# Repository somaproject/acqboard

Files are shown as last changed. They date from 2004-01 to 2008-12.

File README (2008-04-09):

pcb/
    All Protel-related files for schematic capture and board design

docs/
    Documentation, including Adobe Illustrator design documents,
    graphs from final filter responses, and comments on design decisions
docs/filters
    Filter design and analysis and simulation code

vhdl/
    main system vhdl

sim/
    code to simulate the vhdl, and for spice sims
    .do files
    simulated parts (acqboard, etc)
    analysis of the output

tgt/ 
    Final aggregate project, compiled outputs, filters, bitstreams, etc. 

tests/ 
   code to test various parts of the system in the real world -- i.e. hardware tests, etc. 

tests/vhdl : 
   bits of vhdl for testing
tests/analysis : 
   code to analyzie the resulting output
tests/results :
   result data, result figures, result commentary
tests/acqboardcmd:
   program for interfacing with protoboard acqboard domain sockets
tests/benchmarks:
   The actual benchmarks; this is the code that generates and saves the results of a series of runs in HDF5 format. These files are saved to results, and analysized with analysis

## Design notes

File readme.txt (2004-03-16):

To do:

Change ADC buffer amps + filter stage into RRIO op-amps
Figure out some solution to the voltage problem. 

Simulations of butterworth input amps

So, there's this problem in that the system, as designed, uses non-RRIO adc buffer op-amps (the AD8021). This sucks, a lot. 

Because if we want to level-shift our input +-2.5 to 0-5V unipolar, we need a RRIO buffer. Plus, there are (IMHO) issues with the adc reliably sampling stuff that gets too close to its rails. 

So, ideally, the ADC could sample 0-4.096 V, and the inputs could be limited to +-2.048 V. Which is great, just switch in a new voltage regulator. We'll still
have to design-in a new buffer amp, but whatever, it may not really need to be RRIO if it can go to within 1V of the rails. 

But how do we find a 1.024V  voltage reference fto bias the buffer OAs?. Accuracy (as in initial, and TCO) isn't that big of a deal because it will
all be taken care of digitally. But the Ibias Is pretty high, and i'm not sure how it varies with amplitude, etc. 

Now, to pick a new Op-Amp:

part	price/160  Ibias (nA)	Vnoise	Voffset	SFDR	notes
AD8027		   4000/6000	
AD8510		   0.075				input v from -2 to +2.5
AD8671		   40		3	75		VOUT too low
AD820							Crappy THD+N
AD8651							VOUT too low
AD8627						-90 

Ha ha, we can just use the AD8027 :) We just need to buffer the voltage-divided reference through an OA. Although, ass, it's performance is mediocre in the THD+N measurement. 

However, the AD8519 supposedly has THD+N in unity gain of 120 dB, although there aren't really graphs. But it will most certainly work as an ADC driver, assuming that the voltage inputs aren't an issue. 

Now, for some math: 
our voltage reference is accurate to 0.1%, and drifts at 25 ppm/C
Resistors for dividing: 0.1%, drift 25 ppm/c

After contacting people, it looks like I may just be SOL wrt getting tempco-matched resistors.  But I can find 25ppm/C ones. 

Now, let's assume values of 10k each, and let's assume that TCo is positive. Now, the tempcos are potentially going to co-vary, because they are in close physical proximity. But ignore that -- let's assume R2 stays constant, and R1 varies at 25 ppm/C, for maximum difference. That works out to Vout = Vin(1+Tco)/(2+Tco), or (for 25 ppm/c) roughly 6 ppm/C. This puts a lot of the responsibility for stability on the voltage reference. We can use a OPA227 to buffer the output. 

--------------------------------------------------------------------------
Soma Command configuration
--------------------------------------------------------------------------
The soma command interface over fiber is spartan at best. 

Each transmit packet has a CMDST byte, a CMDID byte, and a CHKSUM byte.

The acqboard can be in one of three modes:
    Mode 0: normal mode, acquiring and filtering data. 
    Mode 1: offset disable -- dc offset compensation is disabled
    Mode 2: disables the input and disables offsets. Just outputs programmed sample buffer. 

Each of these modes has a "loading" bit.

Note that there is this "problem" with there only being one acqboard interface but two DSPs. this means channel modification commands have to be very careful!!!

--------------------------------------------------------------------------
So, general system properties, etc: 

AD8221 has amazing stuff... the new data sheet is an inspiration to all of humanity!

--------------------------------------------------------------------------
AA Filter component value selection:
--------------------------------------------------------------------------

For the LTC1653-3, the equation is:
R = 10k * (256kHz)/Fc; 

from the dsp folder:

The first filter has a -3 db at 10056.32 Hz
The second filter has a -3 db at 29829.14 Hz
The combined (both) filter has a -3 db at 9605.82 Hz
The combined (both) filter has a -96 db at 129371.07 Hz

We assume that their Fc == -3 dB point, thus 
The LTC1563-3 Resistors are 255k , part 9C08052A2553FKHFT from digikey

---------------------------------------------------------------------------
input stage
---------------------------------------------------------------------------
499 0hm .5% \0805 resistors, RR12P499DCT-ND from digikey

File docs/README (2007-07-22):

    * Overview

    *CHAPTER 1 Problem formulation (Design goals and overview)
          o What our real goal is
          o The importance of
                + Linearity
                + Linear Phase
                + Low-noise
                + High common-mode rejection
                + potential DC accuracy?
                + Bandwidth?
                + Resolution
          o Size?
          o Programmable Gain
          o Cost?
          o Number of channels
      
          o Electrical Isolation -- the challenges of mixed-signal design

    * CHAPTER 2 signal chain design -- all design data 
      -- these are all the design specs; there is no empirical data here at all
      * schematic of signal channel 
      * input: In-Amp -- component and performance
      * Amplification : PGA, filter
         * gain settings / voltage ranges
      * Continuous channels: 
      * A->D:
         * Hardware Filter design:
	   o We desire 16-bit resolution with an input bandwidth of 10 kHz. 
	   o to achieve this, we oversample, downsample, and filter
	
         * digital filtering 
	   * digital filtering simulation
	   * fixed-point math 

    * CHAPTER 3 Measured performance:
      1. CMRR  
      2. Noise
      3. THD+N 
      4. linearity 
      5. Rat Data

    * CHAPTER 4 Board operation and fiber IO 
          o four modes
            1. describe modes
          o output interface
          o input interface and bus protocol
          o actual commands
	  o front and back interfaces? 
    * CHAPTER 5 digital hardware implementation -- A tour of the FPGA
          o FPGA selection
          o Digital offsets
          o fixed-point math
          o Commands
          o Optical Interface
          o Modes
          o EEPROM functionality

    * CHAPTER 6 Circuit Design Commentary, hardware
 	* Schematics, what they mean? Component identification?
 	* PCB Layout 
 	  * composit diagram -- tour, showing modules, layers
   	  * ref appendex in the back 
        * BOM
        * Component identification
	* enclosure
  	
    * Additional Results
          o [additional simulation notes]
          o Tests on:
                + Analog performance, using Chris's hardware (?)
                + Single-channel
                + multi channel
                + Real Rat

Albert suggests appendix

    * THD+N measurement mechanism
    * Oversampling, downsampling, etc. 
    * Filter design code, analysis
    * 

Points we'll want to be sure to discuss someplace: 
Component identification process
Parameters measured
VHDL organization
unit tests
Raw mode
offset calibration

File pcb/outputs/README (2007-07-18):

the files are

acqboard.GTO : top silkscreen
acqboard.GTS : top soldermask
acqboard.GTL : top solder layer
acqboard.GP1 : internal plane 1
acqboard.GP2 : internal plane 2
acqboard.GBL : bottom solder layer
acqboard.GBS : bottom soldermaskk
acqboard.GBO : bottom silkscreen
acqboard.TXT : drill file

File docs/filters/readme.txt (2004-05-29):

-- files in this directory
analogfilters.m : calculations and graphs of the analog filters on the board,
		 and combines them with an in-memory variable called "h", 
		 that is, the impulse response of the FIR decimating filter. 

fxquant.m : _so_ not my code. code to quantize the coefficients in an intelligent way. 
	  
vect_to_block_22 : takes a vector of type double normalized to between -1 and 1, quantizes the values to acceptable 22-bit twos-complement fixed point values, and then writes out those values in hex optimized for copying into blockselect+ ram. 

------------------------------------------------------------------------------
Signal processing related to the Soma acquisition board. 

First, we need a digital low-pass decimating filter which will (for data sampled at 256kHz) pass t400o 10 kHz with as little ripple as possible, and stop at 16 kHz down by ~85 dB. Why 85 db? The analog filters have already attenuated atthat point, and monotonically attenuate after that.  

Oh, and max it can only be 120 taps long. 

h_01.mat : good example of filter.
h_02.mat is another good example. The problem is that we still aren't getting the response we want, but this'll be good enough. 

for our analog filters, they are approximated by:

[bf2, af2] = besself(2, 38000);
[bf1, af1] = besself(4, 15250);

such that :

The first filter has a -3 db at 10056.32 Hz
The second filter has a -3 db at 29829.14 Hz
The combined (both) filter has a -3 db at 9605.82 Hz
The combined (both) filter has a -96 db at 129371.07 Hz

Using the equations fomr SLOA049A for a second-order bessel with:
order 2
FSF=1.2736
Q=.5773

we know R2=R1, thus the big variables are R2, R3, C1, and C2. 
Fc=1/(FSF*2*pi*Q*(R3*C1+R2*C1+R3*C1)); 
C2=(Q*(R3*C1+R2*C1+R3*C1))^2/(R2*R3*C1)
so (per the app note)

R2=1.870 k = R9 = R8
R3=1.870 k = R10
C1=1300 pF = C42
C2=3900 pf = C44

-----------------------------------------------------------------------------
more DSP
-----------------------------------------------------------------------------

note that the output ft following decimation is

Y_d(e^{j\omega}) = \frac{1}{M}\sum_{i=0}^{M-1}X(e^{j(\frac{\omega}{M}-\frac{2*pi*i}{M})})

I.e. added, replicated copies. Thus, we created the function downspectra, which adds the spectra of a filter h[n] downsampled by N, scaled by the appropriate amount, and returns the result, from 0 to pi. 

As we can see from the output of downspectra.m, the aliased images suck a lot more than we had originally anticipated, because there are 7 of them adding up. Thus, it's not enough to make sure our signal outside of the bandwidth of interest is down by 96 db, but rather need an ADDITIONAL 15 dB down!

But, we only care about the region in DC-10 kHz, correct? So... 

First, we created some code to let us look at downsampled filters.

Then, we realized that we could:
B = remez(119, [0 10/128  22/128 1], [1 1 0 0 ], [0.5  1000]);
I.e. create a filter with a not-as-tight passband. this results in us getting part of a high-frequency image in our output, but "who cares", as we're only interested in the band between 0-10 khz. This will mean, however, that all DSP boards will need to have an O(10) tap filter to further filter. Oh well. 

Part of me still wishes there were a better way. I'm just not seeing it though. But, happily, we now have correct output plots of the signal versus alias/noise for the total system. 

The better way was to allow filters of length 144. 

If we allow filters of this length, then we can alias-away the problems.

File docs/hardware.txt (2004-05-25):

To do:

Change ADC buffer amps + filter stage into RRIO op-amps
Figure out some solution to the voltage problem. 

Simulations of butterworth input amps

So, there's this problem in that the system, as designed, uses non-RRIO adc buffer op-amps (the AD8021). This sucks, a lot. 

Because if we want to level-shift our input +-2.5 to 0-5V unipolar, we need a RRIO buffer. Plus, there are (IMHO) issues with the adc reliably sampling stuff that gets too close to its rails. 

So, ideally, the ADC could sample 0-4.096 V, and the inputs could be limited to +-2.048 V. Which is great, just switch in a new voltage regulator. We'll still
have to design-in a new buffer amp, but whatever, it may not really need to be RRIO if it can go to within 1V of the rails. 

But how do we find a 1.024V  voltage reference fto bias the buffer OAs?. Accuracy (as in initial, and TCO) isn't that big of a deal because it will
all be taken care of digitally. But the Ibias Is pretty high, and i'm not sure how it varies with amplitude, etc. 

Now, to pick a new Op-Amp:

part	price/160  Ibias (nA)	Vnoise	Voffset	SFDR	notes
AD8027		   4000/6000	
AD8510		   0.075				input v from -2 to +2.5
AD8671		   40		3	75		VOUT too low
AD820							Crappy THD+N
AD8651							VOUT too low
AD8627						-90 

Ha ha, we can just use the AD8027 :) We just need to buffer the voltage-divided reference through an OA. Although, ass, it's performance is mediocre in the THD+N measurement. 

However, the AD8519 supposedly has THD+N in unity gain of 120 dB, although there aren't really graphs. But it will most certainly work as an ADC driver, assuming that the voltage inputs aren't an issue. 

Now, for some math: 
our voltage reference is accurate to 0.1%, and drifts at 25 ppm/C
Resistors for dividing: 0.1%, drift 25 ppm/c

After contacting people, it looks like I may just be SOL wrt getting tempco-matched resistors.  But I can find 25ppm/C ones. 

Now, let's assume values of 10k each, and let's assume that TCo is positive. Now, the tempcos are potentially going to co-vary, because they are in close physical proximity. But ignore that -- let's assume R2 stays constant, and R1 varies at 25 ppm/C, for maximum difference. That works out to Vout = Vin(1+Tco)/(2+Tco), or (for 25 ppm/c) roughly 6 ppm/C. This puts a lot of the responsibility for stability on the voltage reference. We can use a OPA227 to buffer the output. 

--------------------------------------------------------------------------
Soma Command configuration
--------------------------------------------------------------------------
The soma command interface over fiber is spartan at best. 

Each transmit packet has a CMDST byte, a CMDID byte, and a CHKSUM byte.

The acqboard can be in one of three modes:
    Mode 0: normal mode, acquiring and filtering data. 
    Mode 1: offset disable -- dc offset compensation is disabled
    Mode 2: disables the input and disables offsets. Just outputs programmed sample buffer. 

Each of these modes has a "loading" bit.

Note that there is this "problem" with there only being one acqboard interface but two DSPs. this means channel modification commands have to be very careful!!!

--------------------------------------------------------------------------
So, general system properties, etc: 

AD8221 has amazing stuff... the new data sheet is an inspiration to all of humanity!

--------------------------------------------------------------------------
AA Filter component value selection:
--------------------------------------------------------------------------

For the LTC1653-3, the equation is:
R = 10k * (256kHz)/Fc; 

from the dsp folder:

The first filter has a -3 db at 10056.32 Hz
The second filter has a -3 db at 29829.14 Hz
The combined (both) filter has a -3 db at 9605.82 Hz
The combined (both) filter has a -96 db at 129371.07 Hz

We assume that their Fc == -3 dB point, thus 
The LTC1563-3 Resistors are 255k , part 9C08052A2553FKHFT from digikey

---------------------------------------------------------------------------
input stage
---------------------------------------------------------------------------
499 0hm .5% \0805 resistors, RR12P499DCT-ND from digikey

----------------------------------------------------------------------------
High pass Filter
----------------------------------------------------------------------------
Goals:
We use the OPA227UA in-amp as a 2-pole HPF

Rational for design: Assume that there's a 5 V difference between the output node and the input pin of the opamp. That means that there's a 5V drop across Ron+R1. But, then, the voltage across Ron varies as Ron/(Ron+R1). I.e. if R5 = 5k, ad max Ron = 50 ohms, then Ron will see 1/100th the voltage difference, and (as far as I can tell from the 

We end up with a first-order HPF with a pole at 1/RC. Assume Rs = 5k, and thus, we want HPF at:

50 Hz	 0.82 uF
200 Hz   0.22 uF
500 Hz = 0.12 uF

----------------------------------------------------------------------------
FPGA to S-3 in a day!
----------------------------------------------------------------------------
18 April 2004
So, today I'm going to explore the possibility of switching tothe 100-pin Spartan-3 -50 device. Why? 

1. A pack of 24 is only $18.00 each, and that price will come down
2. In 3 years, I'm sure they'll still be around, but cheaper. 
3. since I can get a large quantity now, availability isn't as much of a concern
4. They have dedicated 18x18 hardware multipliers, which should actually save me a lot of space. 
5. I'm wasting time worrying about this "does it fit" mentality -- I hope the mulipliers will save me enough space that the device will easily fit in this logic.  
6. They have a ton more ram (4x) which enables longer filters. This is a good thing because at the moment, I'm capped at a 120-tap filter. This sucks, because it will force me to use the approach for output frequency response I was considering earlier. 

basically, I don't just want stuff down by 96 dB at the 16 kHz edge, because 7 additional copies of the stopband are going to alias into my passband. But given length constraints on h[n], it was impossible to get a FIR filter with a stopband ~-110 dB down. The solution was to push the stopband start out to 19 khz, which would yes, allow for aliasing into the 10-16 kHz region of up to -20 dB. But we only cared about the 0-10kHz region.

Why this is a poor design decision: your output, by design, will have aliasing in the 10-16 kHz range, meaning that the output of the acqboard isn't "safe", i.e. it would need knowledgable post-processing to deal properly. 

Switching to a Spartan-3 lets me eliminate this by using a longer filter, giving me the 10-16 kHz response I need. 

7. It shouldn't take very long to make the switch; go modular design!

The multiplier in the current design (not including the accumulator) takes up 342 slices, i.e. 312 flip flops and 366 LUTs. That's 44% of the design!

There are three things we'll need to change:
1. RMAC hardware: 
    switch multiplier to use the 18x18 hardware mults
    change expected pipeline delay
    So, it looks as if, since XST is inferring things correctly, we don't need to actually explicitly declare them. This strongly suggests that our pipeline delays haven't changed either. 

2. Buffers.
   Each BlockSelect+ ram block has 4x the ram of one in a Spartan-IIE, but there are half as many. The net result is that we have double the ram we did before. We want to effectively double the amount of storage for each buffer, i.e. 256 16-bit words. This means each BlockSelect+ ram block can hold 4 buffers. We will need 3 of them to store all sample buffers. This will also necessitate widening the AIN, AOUT busses from 7 to 8 bits. 
  Added extra pipeline stage to meet timing requirements. 
3. Filter
   Simple to do with a single buffer. 
  Added extra pipeline stage to meet timing requiremetns. 

4. EEPROM interface
   Remapped some of the EEPROM so the loader can still sequentially load stuff. 
5. Control
   Had to be modified as a result of the new EEPROM addrs. Note now that we use DATA[7:0] 

Debug -- adding an extra mode. We're going to add a new "RAW" mode that will just take a single channel and output all of its 256 ksps.

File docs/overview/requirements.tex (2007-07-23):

\section{Requirements}
The Acquisition Board was designed with multiunit electrophysiology in
mind. Below is an explanation of the various design parameters as well
as the context within whcih they are evaluated.

\subsection{Differential Amplification}
All electrophysiological measurements are measurements of an electric
potential -- a voltage. This voltage must be measured between two
points, Va and Vref (the latter being a reference). Frequently
additional sources of voltage relative to ground are present on both
of these inputs, generated by uncontrolled environmental sources. This
\textit{common-mode voltage} is common to both inputs, and is ultimately
removed by the differential amplification.

In practice, manufacturing tolerances prevent complete removal of
common-mode voltage. The ability of a differential amplifier to remove
common-mode voltage is expressed as a ratio of...

\subsection{Input range, amplification, and resolution}

The potential voltages encountered in neural systems can
vary over orders of magnitude. Even when measuring the same
phenomina, differences in electrode configuration and reference
placement can result in a tenfold difference in required
amplification. Thus, electrophyisology amplifiers are equipped
with programmable gain amplifiers, allowing a selection of input
amplifications. 

The existing equipment in MWL allows for 12-bit sampling
of input voltages with full-scale 20 mV (gain = 1,000) to 500 uV
(gain = 40,000). This allows for LSB sizes between 4.8 mV and
122 nV, although system noise performance makes the latter
number unattainable.  

\subsection{Bandwidth}

Electrophysiological phenomina in the brain can be losely divided into
high-frequency, discrete events and low-frequency, continuous signals.
Neural action potentials ("spikes") comprise the first category, with
frequencies of interest between 1 kHz and 8 kHz. Electroencephalogram
and local field potentials are believed to be the aggregate
synchronous activity of large brain regions, and make up the bulk of
the latter group. These slower-wave signals extend from 200 Hz down to
near-DC levels.

Thus any electrophysiological system will need to be able to isolate
the higher-amplitude, low-frequency EEG from the low-amplitude,
high-frequency spikes, and do so using controlled filtering that
prevents saturation of analog-to-digital converter input. An aggregate
bandwidth of 10 kHz is thus necessary.

\subsection{Noise}
Even in the absence of any common or differential input, all
amplifiers still generate internal electrical noise, which is measured
relative to the input. This noise corrupts input signals and is
generally broadband, thwarting computaitonal attempts at removing it.
Input noise can directly contribute to cluster size for multiunit
recordings, making unit isolation more difficult.

Our current amplifiers have a manufacturer-measured RTI noise of 20 uV
peak-to-peak. This can have a substantial impact on recorded peak
amplitude of a common 200 uV spike. Ideally, Soma would cut this noise
amplitude down by a factor of 10.

\subsection{Phase}
 The importance of linear phase

\subsection{Electrical isolation} 

\subsection{Cost, size, number of channels}

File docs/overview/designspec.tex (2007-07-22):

Soma is designed to provide differential amplification with high
common-mode rejection of electrophysiological siganals. Each
Acquisition Board provides programmable amplification from 100-10,000
for 8+2 channels. The board itself has an optional early-stage
highpass filter to make maximal use of the dynamic range when
recording high-frequency low-voltage events (spikes) in the presence
of low-frequency high-voltage signals (eeg).

The total system bandwidth is DC-10kHz, with linear phase across the
entire region. The output data stream provides sixteen bits of
resolution per channel at 32 ksps. All data to and from the board is
carried via inexpesnive plastic optical fiber, allowing for complete
electrical isolation between the recording preparation and the rest of
the Soma system.

The eight input channels are grouped into two sets (A and B) of four,
with a fifth channel (AC or BC respectively) allowing independent
filtering and sampling of any of the associated A1-A4 and B1-B4. This
gives rise to the $8+2$ output channels.

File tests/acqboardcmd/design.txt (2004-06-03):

We have two socket classes:
   AcqSocketOut: connects to /tmp/acqboard.in, sends the command that we form
   AcqSockStat: reads /tmp/acqboard.status, detects status changes

AcqState: keeps acqboard state in the GUI:
    Call update_gain(chan, value) to update gain display
         update_hpf(chan, value) to update hpf display

class AcqBoardCmd keeps track of the current command state of the acqboard, andprovides the reference implementation for commands. 

We send a command by getting the
   result = cmd.setgain(chan, value) 

which will have the incremented command ID in it. Then, we wait for status to update the cmdid. 

We would also like to be able to point to a file of 16-bit ints and

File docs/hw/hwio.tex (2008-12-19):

\subsection{Front Panel}

The front panel of the acquisiton module has the 20-pin input for all
8 differential channel pairs of amplifier input.

The pinout can be seen in figure \ref{inputconn}. 

\begin{figure}[h!]
\centering

\caption{The front panel connector for the Soma Acquisition Module.
  AGND is connected to the amplifier analog ground.  }
\label{inputconn}
\end{figure}

The connector is a dual-row, twenty-pin 0.100-inch pitch IDC
connector.

\subsection{Back Panel}
The back panel (Figure \ref{backpanel}) contains power, IO, and
debugging information. There are four sections of interest.

\begin{figure}[h!]
\centering

\caption{The back of the Soma Acquisition Module.}
\label{backpanel}
\end{figure}

\subsubsection{Status LEDs}
There are two status LEDs on the back of the module:
\begin{itemize}
\item \textbf{Link} : indicates the link with the Soma backplane (over the optical fiber)
is functioning properly. 
\item \textbf{Command}: Flashes briefly every time the Soma Backplane sends a command to the 
acqboard. 
\end{itemize}

\subsubsection{JTAG port}
The JTAG port (figure \ref{jtag}) is the standard 14-pin 2mm-pitch JTAG connector for
Xilinx FPGAs, allowing both programming of the on-board flash and
debugging.

\begin{figure}[h!]
\centering

\caption{The JTAG port.}
\label{jtag}
\end{figure}

\subsubsection{Optical Fiber IO}
The optical fiber interface (figure \ref{fiber}) takes two 1-mm
visible-light wavelength plastic optical fibers. These are color-coded
by TX and RX ends to avoid polarity mistakes.

\begin{figure}[h!]
\centering

\caption{The optical fiber interface.}
\label{fiber}
\end{figure}

\subsubsection{Analog and Digital Power}
Powering analog and mixed signal data acquisition devices is always a
challenge, as the exact nature of the power distribution scheme can
substantially impact analog performance. The power connectors mate
with a Molex 39-01-4041 four-pin connector (and associated female pins
44476-3112).  

The Acquisition module completely isolates its internal analog and
digital power supplies for maximum signal integrity. The digital power
supply requires 5 Volts DC. Analog requires a very clean bipolar +/-5V
DC. See figure \ref{power} for details. 

\begin{figure}[h!]
\centering

\caption{The analog and digital power ports. DVDD=+5V, AVDD=+5V, AVSS=-5V. }
\label{power}
\end{figure}

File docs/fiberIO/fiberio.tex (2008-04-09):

\section{Operation and interfacing}

The acquisition board has four modes of operation, one normal
multichannel mode, one mode for offset compensation, one mode for link
testing with simulated output, and one mode for single-channel test.

Interfacing with the Acquisition board is accomplished via a plastic
optical fiber interface for enhanced electrical isolation even over
long data transmission distances.

\section{Modes}
The acquisition board has four modes of operation, designed to set the
internal state and prevent accidental configuration modification
during operation.

\subsection{Normal acquisition mode}
Mode 0 is the normal acquisition mode; in this mode all 10 channels
are sampled at the full normal sampling rate and the data is
transmitted over the 8b/10b bus using the standard Encoding Scheme. In
this mode, gain and hardware filter settings can be changed, but
nothing else.

\subsection{Offset disable mode}
Offset disable mode (mode 1)  disables the internal offset compensation. The
values transmitted are thus the actual measured ADC values. This is
the only mode in which new offset values can be saved to the board's
internal non-volatile memory (EEPROM).

\subsection{Input disable mode}
Input disable mode (mode 2) disables all reading from the ADCs; in
this mode no change of input or analog settings has any effect on the
board. While in this mode, the board will continuously transmit a test
pattern stored in the on-board EEPROM.

In this mode, both the test pattern and the digital low-pass filter
can be modified and written to. The sample pattern \textit{is} filtered by
the digital filter, and can be used as a mechanism to verify that the
filter coefficients were properly written.

\subsection{Raw mode}
Raw mode (mode 3) simply outputs the raw, unfiltered, non-decimated
data from a single selected channel. The 192 ksps data stream occupies
multiple words in the transmitted data stream. This can be useful to
characterize the analog properties of a given channel, and to debug
signal integrity problems.

\section{Fiber IO}
The Acquisition Board's external interface is a bidirectional 8 MHz
fiber-optic link over  1mm plastic optical fiber. Both the TX
and RX streams are encoded using 8b/10b encoding.

The Acqboard transmits an 8b/10b-encoded frame of 24 bytes, preceded
by the K28.5 comma character. The nominal frame transmission is as
follows:

\begin{figure}[h!]

\end{figure}

CMDST is a 3-bit field; CMDST[1:0] are the mode numbers; CMDST[0] is
high \textit{after we have just switched into this mode, while this
  mode is loading.} Mode switching is not instantaneous because the
board needs to read values from EEPROM, a (comparatively) slow
process.

Every command sent has a 4-bit command id (CMDID); when a command is
\textit{done executing} the output command id is changed to reflect
this. CMDRP is the command response field; CMDRP[4:1] are the bits of
the most-recently executed CMDID; CMDRP[0] tells whether or not this
command was successful.

The data fields are 1.15-bit twos-complement fixed point samples from
their corresponding ADCs; they are transmitted MSB first.

\emph{Normally, the acqboard receives a stream of valid 8b/10b encoded
  zeros; a new command is signalled by the presence of the comma
  character in the data stream followed by a packet. } which looks as follows:

\begin{figure}[h!]

\end{figure}

\section{Commands}

The following commands are valid in any mode

\subsection{Universal Commands}

\subsubsection{Switch Mode}
\begin{figure}[h!]

\end{figure}

Switch the current acqboard mode to \textsc{mode}. If changing to the RAW mode, the \textsc{chan} field is the 4-bit number of the raw channel you are reading from -- otherwise the field is ignored. 

Note that some mode transitions can take up to 300 ms; during this time the transmitted packet's CMDST will reflect the new mode, but the ``loading'' bit will be set until the mode has been entered. Only once loading is completed will the CMDID be updated. 

\subsubsection{Set Gain}
\begin{figure}[h!]

\end{figure}

Sets the gain of channel \textsc{Chan} to one of the preset gain values \textsc{Gain}. Valid in all modes. 

\subsubsection{Set Input}
\begin{figure}[h!]

\end{figure}

Select which of the four channels will be used for tetrode a and B's continuous channel. 

\subsubsection{High Pass Filter Enable}
\begin{figure}[h!]

\end{figure}

Enable (\textsc{filter}= 1) or disable (\textsc{filter}=0) the high pass filter on channel \textsc{chan}. 

\subsection{Mode 1 Commands}
\subsubsection{Write offset}
\begin{figure}[h!]

\end{figure}

This command writes the 16-bit twos-complement value in V as the
digital offset for channel \textsc{chan} when the gain on that channel
is set to \textsc{gain}. This is only valid in offset-disable mode as
to properly measure the zero offsets you'd need to have offsets
disabled.

\subsection{Mode 2 Commands}
\subsubsection{Write filter}
\begin{figure}[h!]

\end{figure}

This command writes the 22-bit twos-complement value in V as the
\textsc{addr}th coefficient for the low-pass filter.

\subsubsection{Write Sample Buffer}
\begin{figure}[h!]

\end{figure}

This command writes the 16-bit twos-complement value in V as the
\textsc{addr}th sample in the no-input sample buffer.

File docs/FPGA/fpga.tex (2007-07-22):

The Xilinx Spartan-3 is used for acquisition control, digital
filtering, and data encoding and transmission.

\begin{figure}[h!]

\end{figure}

\section{Clocks}
\import{.}{clocks.tex}

\section{The Filter Chain}
\import{filter}{input.tex}
\import{filter}{samplebuffer.tex}
\import{filter}{filterarray.tex}
\import{filter}{rmac.tex}

\section{Input / output}

\import{io}{io.tex}

\section{Control}

\section{Storage}
\import{.}{eepromio.tex}

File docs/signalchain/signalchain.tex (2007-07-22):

This chapter outlines the design and implementation of the primary
soma signal processing chain, from low-level differential input to
encoded binary data at the output of the fiber interface. This is a
design chapter only; all figures are from simulation and design
specifications. For full performance specs, see \ref{NEXTCHAPTER}.

The soma acquisition board signal chain (Figure \ref{signalchain}) can
be partitioned into an analog signal conditioning section and a
digital signal processing section. Here, the stages will be discussed
independently, except where they overlap and integrate to produce the
final output.

\begin{figure}
  \begin{center}
    
    \caption{The Soma 8+2 Acquiusition signal processing chain
      overview.}
    \label{signalchain}
  \end{center}
\end{figure}

\section{Input Differential Amplification}

The AD8221 In-amp is used to provide high common-mode rejection. See
figer foo for a plot of the CMMR of the input stage. This stage has a
constant gain of 100.  To accomodate the large DC offsets inherent in
most electrophysiology recording environments, the inputs are
AC-coupled.

\section{Optional analog high-pass filtering.}
Waveform data (EEG) is low-frequency data in the mV range; spike data
is high-frequency data in the hundreds-of-uV range. When recording
spikes the low-frequency EEG could potentially saturate our amplifier;
thus we have an optional single-pole high-pass filter ($f_{-3dB}=300
Hz$) that can be enabled to maximize spike acqisition dynamic range.

FIGURE Frequency response of the board below 1 kHz with and without --
theoretical

\section{Programmable gain}
The programmable gain amplifier can be off ($g=0$) or set to a range
of gains from 1 to 100; the table below shows the PGA gain, total
system gain, maximum input voltage, and LSB size for the possible
settings.

\begin{table}
\begin{centering}
\begin{tabular}[h!]{|c|c|c|c|}
\hline
PGA gain & Total Gain & Input Voltage Range & LSB size \\
\hline
1 & 100 & $\pm20.480$ mV & $625$ nV \\
2 & 200 & $\pm10.240$ mV & $312$ nV \\
5 & 500 & $\pm4.096$ mV & $125$ nV \\
10 & 1000 & $\pm2.048$ mV & $62.5$ nV \\
20 & 2000 & $\pm1.024$ mV & $31.3$ nV \\
50 & 5000 & $\pm0.410$ mV & $12.5$ nV \\
100 & 10000 & $\pm0.205$ mV & $6.3$ nV \\
\hline
\end{tabular}
\end{centering}
\caption{Gain settings and voltage levels}
\end{table}

\section{Analog to Digital Conversion}
Signal chain design: to achieve 16-bits with an input bandwidth of 10
kHz we oversample, downsample, and digitally filter. The filtering
process is the combination of the following factors:

\begin{enumerate}
\item an initial antialiasing filter
\item The analog-to-digital conversion step
\item fixed-point FIR filtering
\item downsampling
\end{enumerate}

\subsection{Antialiasing Filter}
The data is initially sampled at 192 kSPS; an 8-pole bessel filter
achieves greater than 96 dB attenuation within the stop-band while
maintaining linear phase (constant group delay) across the passband.

\begin{figure}[h!]
  
  \label{analog.freqres}
  \caption{Anti-aliasing filter total frequency response.}
\end{figure}

\begin{figure}[h!]
  
  \label{analog.pass}
  \caption{Antialiasing filter passband frequency response}
  
  \label{analog.grd}
  \caption{Anti-aliasing filter group delay.}
\end{figure}

\subsection{ADC}
A 16-bit ADC running at $f_s=192 \textrm{kHz}$ samples the incoming antialiased signal. 

\subsection{Filtering}
We filter the sampled data using an N-Tap FIR filter using fixed-point
convolution. We use an extended-precision multiplier, 22-bit filter
coefficients, and an extended-width accumulator to reduce the negative
artifacts present in fixed-point aritmetic.

The Parks-McClellan optimum equiripple FIR filter is used for a cutoff
at 10 kHz; the resulting frequency response (and coefficient-quantized
frequency response) are seen in figure \ref{FIR}. A 143-tap filter
gives the required stopband attenuation while keeping FIR-induced
passband ripple to under $0.5 dB$, while fitting in our allocated FPGA
resources.

\begin{figure}[h!]
  
  \label{FIR}
  \caption{Frequency response of FIR filter.}
\end{figure}

\subsection{Downsampling}
We filter and then downsample; the filtering step is actually only
performed once for every $M=6$ input samples, as the other $M-1$
samples would be removed in the decimation step and thus be wasted.

\subsection{Total response, designed and measured}
The resulting frequency response of the combined analog and digital
filters are shown in figures blah, including zoomed-in passband and
stopband performace. The frequency response following decimation is
also shown, with the sum of the (imperfectly filtered) antialiased
components highlighted.

\begin{figure}[h!]
  
  \label{digital.aggregate}
  \caption{Aggregate pre-decimation signal chain filtering.}
  
  \label{digital.pass}
  \caption{Aggregate pre-decimation signal chain passband.}
\end{figure}

\begin{figure}[h!]
  
  \label{digital.withaliases}
  \caption{Aggregate post-decimation filtering.}
\end{figure}

This concludes the tour of the Soma 8+2 Acquisition board signal
processing chain. The next chapter deals with the resulting empirical
measures from the board, including frequency response, harmonic
distortion, and noise measurements.

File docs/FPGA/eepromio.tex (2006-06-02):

\subsection{EEPROM I/O}

The EEPROM is a SPI-serial component which can store up to 32 kB of ram. We store 16-bit big-endian words as in table \ref{eepromaddr}. 
\begin{table}
\begin{tabular}{cc}
Word Address & Data \\
\hline
0-511 & Filter (256 2-word samples) \\
512 - 757 & sample buffer initial values (256 words) \\
1024 - 1535 & offset values for each gain (512 words) \\ 
\end{tabular}
\label{eepromaddr}
\end{table}

On each operation we execute the EEPROM's write-enable (WREN)
instruction, and then a full two bytes.  Since we have 12 bits of
address, we place the 11 input bits on the line and always have the
LSB be zero.

We use the two-byte read and two-byte write seqence capability of the
eeprom for both reads and writes. We never cross page boundary since
we always start with LSB = 0.

To interface to the SPI EEPROM we use a single output mux driven by
\signal{CNT}.

\begin{figure}[h!]

\end{figure}

\begin{figure}[h!]

\end{figure}

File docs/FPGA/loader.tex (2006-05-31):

\subsection{EEPROM I/O}
The loader simply handles the bulk transfer of data from the EEPROMIO
into the filter array and the sample buffer on mode transition. The
addresses of the EEPROM are decoded into the filter write-enable
(\signal{FWE}) and sample buffer write-enable (\signal{SWE}) signals.

\begin{figure}[h!]

\end{figure}

\begin{figure}[h!]

\end{figure}

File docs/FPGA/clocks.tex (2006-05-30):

\section{Clocks}

The FPGA is clocked at 72 MHz via a DCM-doubled 36-MHz input clock signal. 

A series of centralized synchronized clock-enables coordinates events
across the entire FPGA.

\begin{table}
\begin{tabular}{llll}
  \signal{INSAMPLE} & 375 & 192.0 kHz & Input sample clock enable -- sets the input sampling rate\\
  \signal{OUTSAMPLE} & 2250 & 32.0 kHz & Output sample clock enable -- controls the output sample rate. \\
  \signal{OUTBYTE} & 90 & 800.0 kHz & Output byte clock enable, enables each symbol (encoded byte) on the output fiber interface. \\
  \signal{CLK8} & 9 & 8.0 MHz & Fiber output bit clock.  \\
  \signal{SPICLK} &  180& 400.0 kHz  & SPI clock for interfacing with EEPROM.  \\
\end{tabular}
\end{table}

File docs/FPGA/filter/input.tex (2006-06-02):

\subsection{Input}

The FPGA input module (figure \ref{input}) controls ADC sampling, bit acquisition, offset compensation, and the eventual write-out of the sample bits. 

\begin{figure}[h!]
\begin{centering}
\label{input}

\end{centering}
\end{figure}

\subsubsection{ADC interface}
The two sets of ADCs are serially chained, providing \signal{SDIA} and \signal{SDIB}. The ADC FSM (figure \ref{adcfsm}) controls the sampling sequence; CONCNT the delay between the assertion of \signal{CNV} and the bit read-out; \signal{BITCNT} sends the sample clock. To compesate for the ADC readout delay and the propagation delay across the galvanic isolators, we delay the \signal{LSCK} via a shift-register into \signal{BITEN}. 

\begin{figure}
\label{adcfsm}
\begin{centering}

\end{centering}
\end{figure}

We go out of our way to make sure we keep the digital signals are quite during the ADC's conversion period. 

\subsubsection{Offset arithmatic}
The 16-bit unipolar ACD samples are converted to bipolar samples and then added to the per-channel offset values. The resulting \signal{SUM} is checked for overflow and then written to. 

\subsubsection{Output writing}
For each \signal{INSAMPLE} assertion we cycle through all channels and then write the resulting offset-adjusted values to the downstream modules.

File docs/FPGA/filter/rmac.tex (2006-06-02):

\subsection{Repeated Multiply / Accumulate } 
FIR filtering is performed by the repeated multiply-accumulate module; the filter used is that described earlier. 

\subsubsection{RMAC}
\begin{figure}
\label{rmac}

\caption{Repeated Multiply-Accumulate (RMAC) module for fixed-point convolution.}
\end{figure} 
The repeated multiply-accumulate unit is composed (Figure \ref{rmac}) of the following subcomponents:

\begin{enumerate}
\item \textbf{Sample Counters}: under control of the RMAC FSM, the RMAC drives the sample buffer address pointer \signal{XA[7:0]} and the filter coefficient buffer address pointer \signal{HA[7:0]}. The sample buffer address pointer begins at location \signal{XBASE[7:0]} and counts backwards through the buffer. 
\item \textbf{Multiplier}: The pipelined multipler performs fixed-point multiplication of the input, truncating the output at 1.23 bits of data. 
\item \textbf{Extended-Resolution Accumulator} For each iteration through the sample buffer, the accumulator sums the resulting sample/coefficient products. The arithmetic is done with 7 extra bits of precision on the left side of the decimal, allowing for extended range and to prevent saturation mid-convolution. 
\item \textbf{Convergent Rounding} Convergent rounding of the input is performed, resulting in the output being in ``8.15'' format. 
\item \textbf{Overflow Detection} If the output is too large to be expressed in 1.15 format than the value saturates at either positve or negative extreme. 
\end{enumerate}

The RMAC is controlled by a FSM (Figure \ref{rmacfsm}) that is designed to convolve one channel's data per \signal{STARTMAC}. When \signal{STARTMAC} is asserted, the system convolves up to a maximum length $L$, and then asserts \signal{MACDONE}. 

\begin{figure}
\label{rmacfsm}

\caption{Controlling FSM for the RMAC.}
\end{figure}

\subsubsection{Fixed-point noise model} 
Here we develop a model of the dynamic range. \textbf{TO DO } 

\subsubsection{RMAC control}
The RMAC control (Figure \ref{rmaccontroller}) coordinates filtering
across all 10 channels as well as incrementing the base address of the
sample buffer, thus controlling the output interface of the sample
ring buffer. The associated FSM (figure \ref{rmaccontrollerfsm}) is
equally simple, asserting \signal{STARTMAC} to the RMAC engine and
waiting for completion.

\begin{figure}
\label{rmaccontroller}

\caption{The RMAC controller}
\end{figure}

\begin{figure}
\label{rmaccontrollerfsm}

\caption{The RMAC controller FSM}
\end{figure}

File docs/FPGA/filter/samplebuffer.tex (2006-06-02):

\subsection{Sample Buffer}

The sample buffer stores 256 16-bit samples for each of the 10
channels. The dual-port Spartan-3 BlockRam allows for an independent
interface to simultaneously read out the samples. The assertion of
\signal{ALLCHAN} writes all channels. \signal{CHAN[3:2]} selects which
internal block is used; \signal{CHAN[1:0]} selects whcih range in the
block is written to.

\begin{figure}
\begin{centering}

\end{centering}
\end{figure}

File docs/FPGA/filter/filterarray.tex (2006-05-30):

\section{Filter Array}

\begin{figure}
\label{filterarray}

\end{figure}

The filter array uses a block of BlockRAM to store the 22-bit
fixed-point filter coefficients. The double-buffering allows for
independent read-write points to let the Control and EEPROM write the
coefficents on mode-switch.

Coefficients are written 16-bits at a time as indicated in Figure \ref{filterarray}.

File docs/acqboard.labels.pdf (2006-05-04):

# Soma 8+2 Acquisition

### Eric Jonas <jonas@mwl.mit.edu>

rev: 1.0 | run: Etech-web-20060504
AD8221AR | Analog Devices

## SOIC AR

Precision Instrumentation Amplifier with High CMRR Over

Designators: U12.(1-8), C33, C32

XC3S50-VQ100C | Xilinx
VQ100

Xilinx Spartan-3 FPGA

Designators: U4

HFBR-1528 | Avago Technologies

Plastic Optical Fiber Transmitter

Designators: O1

# Soma 8+2 Acquisition

### Eric Jonas <jonas@mwl.mit.edu>

rev: 1.0 | run: Etech-web-20060504
HFBR-2528 | Avago Technologies

1mm Plastic Optical Fiber 10 Mbd receiver

Designators: O3

# Soma 8+2 Acquisition

### Eric Jonas <jonas@mwl.mit.edu>

rev: 1.0 | run: Etech-web-20060504
SN75451BDR | Texas Instruments

## SOIC

Designators: U3

# Soma 8+2 Acquisition

### Eric Jonas <jonas@mwl.mit.edu>

rev: 1.0 | run: Etech-web-20060504
SSF-LXH2100ID | Lumex

## Dual-LED

DUAL LED 5MM RA 2-WIDE RED PC MNT

Designators: L1

# Soma 8+2 Acquisition

### Eric Jonas <jonas@mwl.mit.edu>

rev: 1.0 | run: Etech-web-20060504
25LC320/SN | Microchip, Inc

## SOIC

32k SPI Bus Serial EEPROM 2MHz max

Designators: U5

# Soma 8+2 Acquisition

### Eric Jonas <jonas@mwl.mit.edu>

rev: 1.0 | run: Etech-web-20060504

## SG-636PCE 36.0000MC0 Epson Electronics America Inc

OSCILLATOR 36.0000MHZ SMD

Designators: O2

# Soma 8+2 Acquisition

### Eric Jonas <jonas@mwl.mit.edu>

rev: 1.0 | run: Etech-web-20060504
XCF01SV020C | Xilinx
VO20

Xilinx PlatformFlash 1 MBit

Designators: U6

# Soma 8+2 Acquisition

### Eric Jonas <jonas@mwl.mit.edu>

rev: 1.0 | run: Etech-web-20060504
AD8510ARM | Analog Devices

## MSOP-8

Precision Low Noise Single JFET Operational Amplifier

Designators: U24, U25, U7.(1-10), U29

# Soma 8+2 Acquisition

### Eric Jonas <jonas@mwl.mit.edu>

rev: 1.0 | run: Etech-web-20060504
ADG619BRM | Analog Devices

## MSOP-8

CMOS +/-5 V/5 V 7 ohm Single SPDT Switches

Designators: U9.(1-10)

# Soma 8+2 Acquisition

### Eric Jonas <jonas@mwl.mit.edu>

rev: 1.0 | run: Etech-web-20060504
LTC6910-1 | Linear Technology

## SOT23-8

Digital PGA, g=0, 1, 2, 5, 10, 20, 50, 100

Designators: U8.(1-10)

# Soma 8+2 Acquisition

### Eric Jonas <jonas@mwl.mit.edu>

rev: 1.0 | run: Etech-web-20060504
IL715-3 | NVE Corporation

## SOIC

Galvanic Isolator

Designators: U14

# Soma 8+2 Acquisition

### Eric Jonas <jonas@mwl.mit.edu>

rev: 1.0 | run: Etech-web-20060504
IL716-3 | NVE Corporation

## SOIC

Galvanic Isolator

Designators: U15

# Soma 8+2 Acquisition

### Eric Jonas <jonas@mwl.mit.edu>

rev: 1.0 | run: Etech-web-20060504
AD8605ART | Analog Devices

## SOT-23

Precision Low Noise CMOS Single Rail-to-Rail Input/Outpu

Designators: U13, U1.(1-10)

103311-5 | Steward

## Header 10x2h

Right-angle 20-pin shrouded header

Designators: JP2

28F0121-1SR | Steward

## 3312 100 Ohm

Ferrite 10A 100 Ohm

Designators: L2, L3

## LM4140CCM-4.1 National Semiconductor SOIC

Low-noise voltage reference, 4.096V

Designators: U28

# Soma 8+2 Acquisition

### Eric Jonas <jonas@mwl.mit.edu>

rev: 1.0 | run: Etech-web-20060504
CD74HC595SM96 | Texas Instruments

## SSOP

8-bit serial-load paralle-out shift register

Designators: U19, U18, U20, U21, U17, U16

# Soma 8+2 Acquisition

### Eric Jonas <jonas@mwl.mit.edu>

rev: 1.0 | run: Etech-web-20060504
GRM1885C1H151JA01D | muRata
0603 150pF 5%

Ceramic Capacitor 50V C0G

Designators: C40.(1-10)

# Soma 8+2 Acquisition

### Eric Jonas <jonas@mwl.mit.edu>

rev: 1.0 | run: Etech-web-20060504
GRM1885C1H271JA01D | muRata
0603 270pF 5%

Ceramic Capacitor 50V C0G

Designators: C39.(1-10)

# Soma 8+2 Acquisition

### Eric Jonas <jonas@mwl.mit.edu>

rev: 1.0 | run: Etech-web-20060504
GRM1885C1H391JA01D | muRata
0603 390pF 5%

Ceramic Capacitor 50V C0G

Designators: C36.(1-10)

# Soma 8+2 Acquisition

### Eric Jonas <jonas@mwl.mit.edu>

rev: 1.0 | run: Etech-web-20060504
GRM1885C1H431JA01D | muRata
0603 430pF 5%

Ceramic Capacitor 50V C0G

Designators: C35.(1-10)

# Soma 8+2 Acquisition

### Eric Jonas <jonas@mwl.mit.edu>

rev: 1.0 | run: Etech-web-20060504
GRM1885C1H122JA01D | muRata
0603 1200pF 5%

Ceramic Capacitor 50V C0G

Designators: C37.(1-10)

# Soma 8+2 Acquisition

### Eric Jonas <jonas@mwl.mit.edu>

rev: 1.0 | run: Etech-web-20060504
GRM1885C1H132JA01D | muRata
0603 1300pF 5%

Ceramic Capacitor 50V C0G

Designators: C38.(1-10)

# Soma 8+2 Acquisition

### Eric Jonas <jonas@mwl.mit.edu>

rev: 1.0 | run: Etech-web-20060504
GRM1885C1H152JA01D | muRata
0603 1500pF 5%

Ceramic Capacitor 50V C0G

Designators: C41.(1-10)

# Soma 8+2 Acquisition

### Eric Jonas <jonas@mwl.mit.edu>

rev: 1.0 | run: Etech-web-20060504
GRM1885C1H222JA01D | muRata
0603 2200pF 5%

Ceramic Capacitor 50V C0G

Designators: C4.(1-10)

# Soma 8+2 Acquisition

### Eric Jonas <jonas@mwl.mit.edu>

rev: 1.0 | run: Etech-web-20060504
GRM1885C1H242JA01D | muRata
0603 2400pF 5%

Ceramic Capacitor 50V C0G

Designators: C42.(1-10)

# Soma 8+2 Acquisition

### Eric Jonas <jonas@mwl.mit.edu>

rev: 1.0 | run: Etech-web-20060504
RC0603FR-077K5L | Yaego America
0603 7.50k 1%

Resistor 1/10W

Designators: R16.(1-10), R14.(1-10), R15.(1-10), R18.(1-10), R24.(1-10), R22.(1-10), R21.(1-10), R20.(1-10)

# Soma 8+2 Acquisition

### Eric Jonas <jonas@mwl.mit.edu>

rev: 1.0 | run: Etech-web-20060504
RC0603FR-0711KL | Yaego America
0603 11.0k 1%

Resistor 1/10W

Designators: R27, R17.(1-10), R25.(1-10), R48, R19.(1-10)

RC0603FR-0712KL | Yaego America
0603 12.0k 1%

Resistor 1/10W

Designators: R23.(1-10)

RC0603FR-075K6L | Yaego America
0603 5.60k 1%

Resistor 1/10W

Designators: R13.(1-10)

## RR0816P-4990-B-T5-68A Susumu Co Ltd

0603 499 0.1%

Resistor 1/16W

Designators: R26.(1-8)

# Soma 8+2 Acquisition

### Eric Jonas <jonas@mwl.mit.edu>

rev: 1.0 | run: Etech-web-20060504
RR0816P-103-B-T5 | Susumu Co Ltd
0603 10.0k 0.1%

Resistor 1/16W

Designators: R29

# Soma 8+2 Acquisition

### Eric Jonas <jonas@mwl.mit.edu>

rev: 1.0 | run: Etech-web-20060504
RR0816P-303-B-T5 | Susumu Co Ltd
0603 30.0k 0.1%

Resistor 1/16W

Designators: R28

# Soma 8+2 Acquisition

### Eric Jonas <jonas@mwl.mit.edu>

rev: 1.0 | run: Etech-web-20060504
C0603C103K5RACTU | Kemet
0603 0.1uF

Chip Capacitor X7R

Designators: C57, C44.(1-8), C55, C53, C52, C51, C50, C71.(1-10), C72.(1-10), C75, C74, C59, C58, C19, C18, C13, C12, C10, C31.(1-10), C16, C15, C14, C47, C17, C43.(1-8), C9, C8, C3.(1-10), C1.(1-10), C32.(1-10), C6, C5.(1-10), C22, C23, C20, C21, C26, C27, C24, C25, C66, C28.(1-10), C29.(1-10), C49, C77, C56, C76

# Soma 8+2 Acquisition

### Eric Jonas <jonas@mwl.mit.edu>

rev: 1.0 | run: Etech-web-20060504
TPS77525D | Texas Instruments

## SOIC

2.5V 500 mA LDO

Designators: U23

# Soma 8+2 Acquisition

### Eric Jonas <jonas@mwl.mit.edu>

rev: 1.0 | run: Etech-web-20060504
TPS70245PWP | Texas Instruments

## TSSOP

Dual-output 3.3/1.2V LDO

Designators: U22

# Soma 8+2 Acquisition

### Eric Jonas <jonas@mwl.mit.edu>

rev: 1.0 | run: Etech-web-20060504
MCR03EZPJ000 | Rohm
0603 0 5%

Resistor zero-ohm

Designators: R45, R44, R47, R46, R39, R43, R34, R35, R36, R37, R31, R32, R33

# Soma 8+2 Acquisition

### Eric Jonas <jonas@mwl.mit.edu>

rev: 1.0 | run: Etech-web-20060504
ECE-V1EA101P | Panasonic - ECG

## E 100uF 20%

Panasonic Capacitor

Designators: C70, C69, C61

# Soma 8+2 Acquisition

### Eric Jonas <jonas@mwl.mit.edu>

rev: 1.0 | run: Etech-web-20060504
RC0603FR-07100KL | Yaego America
0603 100k 1%

Resistor 1/10W

Designators: R50.(1-8), R49.(1-8)

# Soma 8+2 Acquisition

### Eric Jonas <jonas@mwl.mit.edu>

rev: 1.0 | run: Etech-web-20060504
ECJ-1VF1E105Z | Panasonic - ECG
0603 1uF +20/-80%

Capacitor 25V Y5V

Designators: C60

# Soma 8+2 Acquisition

### Eric Jonas <jonas@mwl.mit.edu>

rev: 1.0 | run: Etech-web-20060504
39-30-3045 | Molex

4-pin right-angle header 4.2mm

Designators: POWER-D1, POWER-A1

# Soma 8+2 Acquisition

### Eric Jonas <jonas@mwl.mit.edu>

rev: 1.0 | run: Etech-web-20060504
RC0603FR-0747RL | Yaego America
0603 47.0 1%

Resistor 1/10W

Designators: R5, R6, R1, R41, R40, R42

# Soma 8+2 Acquisition

### Eric Jonas <jonas@mwl.mit.edu>

rev: 1.0 | run: Etech-web-20060504
RC0603FR-07100RL | Yaego America
0603 100 1%

Resistor 1/10W

Designators: R3, R12, R10, R11

RC0603FR-072KL | Yaego America
0603 2.00k 1%

Resistor 1/10W

Designators: R7, R8, R9, R2

RC0603FR-0710RL | Yaego America
0603 10.0 1%

Resistor 1/10W

Designators: R30.(1-10)

RC0603FR-071K87L | Yaego America
0603 1.87k 1%

Resistor 1/10W

Designators: R38

# Soma 8+2 Acquisition

### Eric Jonas <jonas@mwl.mit.edu>

rev: 1.0 | run: Etech-web-20060504
C0805C106K9PACTU | Kemet
0805 10uF 10%

Capacitor X5R

Designators: C73.(1-8), C65.(1-8), C48.(1-10)

# Soma 8+2 Acquisition

### Eric Jonas <jonas@mwl.mit.edu>

rev: 1.0 | run: Etech-web-20060504
T491A106K006AT | Kemet
3216 10uF 10%

Tantalum Capacitor 6.3V

Designators: C45.(1-8), C46.(1-8), C54, C64, C62, C63, C34.(1-10), C2.(1-10), C11, C33.(1-10)

# Soma 8+2 Acquisition

### Eric Jonas <jonas@mwl.mit.edu>

rev: 1.0 | run: Etech-web-20060504
AD8513ARZ | Analog Devices

## SOIC

Precision Low Noise Quad JFET Operational Amplifier RoHS

Designators: U10.(1-10)

# Soma 8+2 Acquisition

### Eric Jonas <jonas@mwl.mit.edu>

rev: 1.0 | run: Etech-web-20060504
84833-1420 | Molex

2.00mm (.079") Pitch Milli-Grid™ Header, Right Angle,

Designators: JP1

# Soma 8+2 Acquisition

### Eric Jonas <jonas@mwl.mit.edu>

rev: 1.0 | run: Etech-web-20060504
ADG604YRUZ | Analog Devices

## TSSOP

1pC Charge Injection, Low Leakage CMOS 4-Channel Multipl

Designators: U11, u27

# Soma 8+2 Acquisition

### Eric Jonas <jonas@mwl.mit.edu>

rev: 1.0 | run: Etech-web-20060504
AD7685BRMZ | Analog Devices

## MSOP

16-bit 250 ksps ADC

Designators: U2.(1-10)

# Soma 8+2 Acquisition

### Eric Jonas <jonas@mwl.mit.edu>

rev: 1.0 | run: Etech-web-20060504
GRM31C5C1E683JA01L | muRata
1206 68000pF 5%

Ceramic Capacitor 25V C0G

Designators: C30.(1-10)

# Soma 8+2 Acquisition

### Eric Jonas <jonas@mwl.mit.edu>

rev: 1.0 | run: Etech-web-20060504
T520T476M006ATE070 | Kemet
3528 47uF 20%

Tantalum Capacitor 6.3V 0.40-ohm ESR

Designators: C67, C7, C68

# Soma 8+2 Acquisition

### Eric Jonas <jonas@mwl.mit.edu>

rev: 1.0 | run: Etech-web-20060504
9C06031A2R70JGHFT | Yaego America
0603 2.7 5%

Resistor 1/10W

Designators: R4

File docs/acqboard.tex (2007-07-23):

\documentclass{book}
\usepackage{fullpage}
\usepackage{sectsty}
\usepackage{somahw}
\usepackage[Lenny]{fncychap}

\allsectionsfont{\sffamily}
\begin{document}

\tableofcontents

\chapter{Overview}
\import{overview/}{requirements.tex}

\chapter{Signal Chain}
\import{signalchain/}{signalchain.tex}

\chapter{Performance}

\chapter{Operation and IO}
\import{fiberIO/}{fiberio.tex}

\chapter{Firmware}
\import{FPGA}{fpga.tex}

\chapter{Circuit Design}

\end{document}

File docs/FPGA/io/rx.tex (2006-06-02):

\subsection{Fiber RX}

The fiber receive interface (figure \ref{fiberrx} ) is in some ways
simpler than the transmit interface. The interface's state machine
(Figure \ref{fiberrxfsm}) waits until we receive a new packet with no
errors and the appropriate K-character, and then sets about latching
the relevant input words.

\begin{figure}[h!]

\label{fiberrx}
\caption{The Fiber Reception interface}. 
\end{figure}

\begin{figure}[h!]

\label{fiberrxfsm}
\caption{The Fiber Reception finite state machine.}
\end{figure}

Any error in 8b/10b decoding or spurious (out-of-sequence) comma
character causes a transition back to \state{NONE}, preventing the
reception of an invalid data frame.

\subsubsection{Decoder}

The deserialization step is somewhat more difficult; as the core is
running at 72 MHz, we can oversample the input bitstream by a factor
of 9. The 8b/10b encoding guarantees a maximum run of five, so we
simply need to maintain a lock for at most five input-bit-cycles.

\begin{figure}[h!]

\label{decoder}
\caption{The oversampling fiber decoder}
\end{figure}

The decoder used here (figure \ref{decoder}) is generalized to work
for different oversampling rates, as it was not known in the early
stage of development what the final oversampling rate would be. We use
a counter which is reset on each bit transition, and shift in the
relevant bits; in the absence of transitions the counter loops and
appropriately samples.

The detection of the unique K28.5 comma character is used to partition
the bits into words via the serial-to-paralllel shift register
\signal{DATAREG}. From that point on we simply count in multiples of
10 bits in gating the output into the 8b/10b decoder.

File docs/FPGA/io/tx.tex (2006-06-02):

\subsection{The Fiber TX module} 

The Fiber TX module (figure \ref{fibertx})  formats data for transmission according to the
Soma FiberIO Protocol. All inputs are latched on the
\signal{OUTSAMPLE} signal to prevent word-skew.

The counter \signal{INCNT} counts the assertion of the input
\signal{YEN} to write samples from the output of the RMAC. These are stored in an appropriate array of registers \signal{YL[n]}.

A giant mux controlled by an \signal{OUTBYTE}-enabled counter multiplex the relevant words into the 8b/10b encoder. 

A simple parallel-load LSB-out shift register takes the 10-bit encoded
data \signal{DOUT} and serializes it to the eventual output
\signal{FIBEROUT}.

\begin{figure}[h!]

\label{fibertx}
\caption{The Fiber Transmission interface}. 
\end{figure}

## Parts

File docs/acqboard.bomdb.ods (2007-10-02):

ACQBOARD Project Summary
Total Device Count |  |  | 40
Quant | Desc | Vendor | Package | Val | Tol | Total | Distributor | Qty
8 | AD8221AR | Analog Devices | SOIC |  | AR | 320 | analog | 392 | $2.74
1 | XC3S50-VQ100C | Xilinx | VQ100 |  |  | 40 | on-hand
1 | HFBR-1528Z | Avago Technologies |  |  |  | 40 | newark | 50 | $10.98
1 | HFBR-2528Z | Avago Technologies |  |  |  | 40 | newark | 50 | $17.19
1 | SN75451BDR | Texas Instruments | SOIC |  |  | 40 | digikey | 50 | $0.60
1 | SSF-LXH2100ID | Lumex | Dual-LED |  |  | 40 | digikey | 50 | $0.75
1 | 25LC320/SN | Microchip, Inc | SOIC |  |  | 40 | digikey | 45 | $0.56
1 | SG-636PCE 36.0000MC0 | Epson Electronics America Inc |  |  |  | 40 | digikey | 50 | $3.13
1 | XCF01SV0G20C | Xilinx | VO20 |  |  | 40 | digikey | 40 | $3.10
13 | AD8510ARM | Analog Devices | MSOP-8 |  |  | 520 | analog | 500 | $1.38
10 | ADG619BRM | Analog Devices | MSOP-8 |  |  | 400 | analog | 450 | $1.10
10 | LTC6910-1 | Linear Technology | SOT23-8 |  |  | 400 | digikey | 500 | $1.53
1 | IL715-3 | NVE Corporation | SOIC |  |  | 40 | digikey | 50 | $6.15
1 | IL716-3 | NVE Corporation | SOIC |  |  | 40 | digikey | 50 | $6.29
11 | AD8605ART | Analog Devices | SOT-23 |  |  | 440 | Digikey | 500 | $1.16
1 | 103311-5 | Steward | Header 10x2h |  |  | 40 | mouser | 50 | $1.45
2 | 28F0121-1SR | Steward | 3312 | 100 Ohm |  | 80 | digikey | 90 | $0.13
1 | LM4140CCM-4.1 | National Semiconductor | SOIC |  |  | 40 | digikey | 50 | $2.72
6 | 74HC595PW-T | NXP Semicondcutor | SSOP |  |  | 240 | digikey | 250 | $0.26
10 | GRM1885C1H151JA01D | muRata | 0603 | 150pF | 5% | 400 | Digikey | 4000 | $0.02
10 | GRM1885C1H271JA01D | muRata | 0603 | 270pF | 5% | 400 | Digikey | 4000 | $0.02
10 | GRM1885C1H391JA01D | muRata | 0603 | 390pF | 5% | 400 | Digikey | 4000 | $0.02
10 | GRM1885C1H431JA01D | muRata | 0603 | 430pF | 5% | 400 | Digikey | 4000 | $0.02
10 | GRM1885C1H122JA01D | muRata | 0603 | 1200pF | 5% | 400 | Digikey | 4000 | $0.02
10 | GRM1885C1H132JA01D | muRata | 0603 | 1300pF | 5% | 400 | Digikey | 4000 | $0.02
10 | GRM1885C1H152JA01D | muRata | 0603 | 1500pF | 5% | 400 | Digikey | 4000 | $0.02
10 | GRM1885C1H222JA01D | muRata | 0603 | 2200pF | 5% | 400 | Digikey | 4000 | $0.02
10 | GRM1885C1H242JA01D | muRata | 0603 | 2400pF | 5% | 400 | Digikey | 4000 | $0.03
80 | RC0603FR-077K5L | Yaego America | 0603 | 7.50k | 1% | 3200 | Digikey | 5000 | $0.00
32 | RC0603FR-0711KL | Yaego America | 0603 | 11.0k | 1% | 1280 | Digikey | 5000 | $0.00 | MCR03EZPFX1102
10 | RC0603FR-0712KL | Yaego America | 0603 | 12.0k | 1% | 400 | Digikey | 5000 | $0.00
10 | RC0603FR-075K6L | Yaego America | 0603 | 5.60k | 1% | 400 | Digikey | 5000 | $0.00
8 | RR0816P-4990-B-T5-68A | Susumu Co Ltd | 0603 | 499 | 0.1% | 320 | Digikey | 400 | $0.18 | RG1608P-4990-B-T5
1 | RR0816P-103-B-T5 | Susumu Co Ltd | 0603 | 10.0k | 0.1% | 40 | Digikey | 50 | $1.51 | RG1608N-103-W-T1
1 | RR0816P-303-B-T5 | Susumu Co Ltd | 0603 | 30.0k | 0.1% | 40 | Digikey | 50 | $1.51 | RG1608N-303-W-T1
142 | C0603C104K5RACTU | Kemet | 0603 | 0.1uF |  | 5680 | Digikey | 8000 | $0.01
1 | TPS77525D | Texas Instruments | SOIC |  |  | 40 | Digikey | 100 | $1.42
1 | TPS70245PWP | Texas Instruments | TSSOP |  |  | 40 | digikey | 50 | $2.70
13 | MCR03EZPJ000 | Rohm | 0603 | 0 | 5% | 520 | digikey | 5000 | $0.00
3 | ECE-V1EA101P | Panasonic - ECG | E | 100uF | 20% | 120 | Digikey | 140 | $0.45
16 | RC0603FR-07100KL | Yaego America | 0603 | 100k | 1% | 640 | Digikey | 5000 | $0.00
1 | ECJ-1VF1E105Z | Panasonic - ECG | 0603 | 1uF | +20/-80% | 40 | Digikey | 100 | $0.02
2 | 39-30-3045 | Molex |  |  |  | 80 | mouser | 100 | $0.57
6 | RC0603FR-0747RL | Yaego America | 0603 | 47.0 | 1% | 240 | digikey | 400 | $0.02
4 | RC0603FR-07100RL | Yaego America | 0603 | 100 | 1% | 160 | Digikey | 300 | $0.24
4 | RC0603FR-072KL | Yaego America | 0603 | 2.00k | 1% | 160 | Digikey | 200 | $0.07 | MCR03EZPFX2001
10 | RC0603FR-0710RL | Yaego America | 0603 | 10.0 | 1% | 400 | digikey | 5000 | $0.00
1 | RC0603FR-071K87L | Yaego America | 0603 | 1.87k | 1% | 40 | Digikey | 200 | $0.08 | MCR03EZPFX1871
26 | C0805C106K9PACTU | Kemet | 0805 | 10uF | 10% | 1040 | Digikey | 3000 | $0.14
1 | PCB |  |  |  |  | 40
1 | ENCLOSURE |  |  |  |  | 40
51 | T491A106K006AT | Kemet | 3216 | 10uF | 10% | 2040 | Digikey | 4000 | $0.07
10 | AD8513AR | Analog Devices | SOIC |  |  | 400 | Digikey | 430 | $4.59
1 | 84833-1420 | Molex |  |  |  | 40 | digikey | 50 | $1.71
2 | ADG604YRUZ | Analog Devices | TSSOP |  |  | 80 | analog | 96 | $2.09
10 | AD7685BRMZ | Analog Devices | MSOP |  |  | 400 | analog | 420 | $8.85
10 | GRM31C5C1E683JA01L | muRata | 1206 | 68000pF | 5% | 400 | Digikey | 2000 | $0.13
3 | T520T476M006ATE070 | Kemet | 3528 | 47uF | 20% | 120 | digikey | 130 | $1.26
1 | 9C06031A2R70JGHFT | Yaego America | 0603 | 2.7 | 5% | 40 | Digikey | 400 | $0.38
1 | NO POPULATE |  | None |  |  | 40
1 | ASSEMBLY | Analog Devices |  |  |  | 40

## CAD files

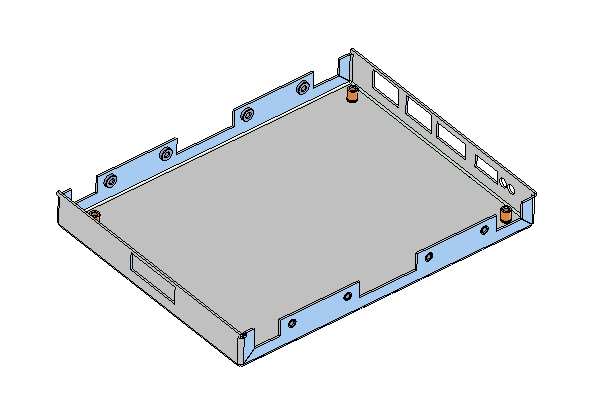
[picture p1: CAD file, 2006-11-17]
enclosure/acqboard.SLDASM
bottom
PEM BSO-632-10 x 4
PEM S-632-2-ZI x 8

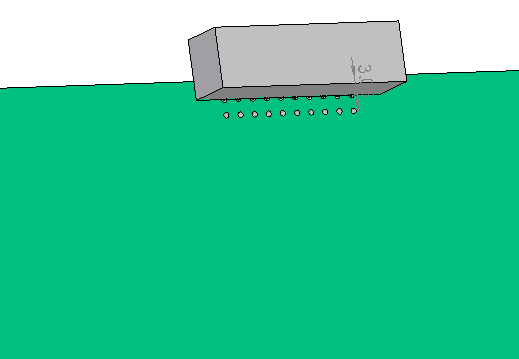
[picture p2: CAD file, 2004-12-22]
enclosure/acqboardpcb.SLDASM
PCB
Amp 103311-5
HFBR-2528 x 2
Lumex SSF-LXH2100ID
molex 87833-142

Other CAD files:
enclosure/bottom.SLDPRT
enclosure/Amp 103311-5.SLDPRT
enclosure/PCB.SLDPRT
enclosure/top.SLDPRT
enclosure/frontback.DWG
enclosure/PEM S-632-2-ZI.SLDPRT
enclosure/PEM BSO-632-10.SLDPRT
enclosure/molex 87833-142.SLDPRT
enclosure/HFBR-2528.SLDPRT
enclosure/Lumex SSF-LXH2100ID.SLDPRT
enclosure/039303045.SLDPRT

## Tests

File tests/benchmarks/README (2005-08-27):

How do we want to do our benchmarks? why are we doing this again? 

I just don't understand. 

There's this notion of an "Experiment". Each experiment consists of an acqboard/function generator in a single common wiring configuration. Note that we also cannot mix raw and simultaneous data within a single file. 

Whatever, stop wasting time on this. 

For a raw file:

we store each channel in /channame/runtype/gain/hpfstatus/

with: 
   runtype == sine, square, noise, etc. 
   gain == the gain of the channel 
   hpfstatus ==   "HPFon" or "HPFoff"

Each table will contain metadata consisting of the 
   1. signal generator settings
   2. board state settings for that channel

what do we want from our RAW interface

s = SineRuns() # simply a container class

s.gains = [] # defalt = 1
s.hpfen = [] # default = off
s.freqs = [] # default = 1 kHz
s.volts = [] # default = 4.0

n = NoiseRuns()
n.chans
n.gains
n.hpfen
n.volts

e = Experiment(filename, note):
e.atsout = unbalanced

e.A1.append(s)
e.A2.append(s) : # append sine run, check if sine run is valid
e.append(n) :

e.run()

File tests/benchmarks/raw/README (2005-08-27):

This is the expeirment design and configuration for running our suite of Raw Benchmarks. 

Each HDF5 file corresponds to an "experiment". An experiment consists of a series of "runs" per channel. It is possible that, between the runs, there is a user-selectable pause to allow manual reconfiguration of some aspect of board parameters. 

States:

use: 

BoardState: object which encapsulates a single channel's baoard state set, and also handles interfacing to the board via iterators

b = BoardState

b.gains = [100, 200, ...]
b.hpfs = [True, False]

e = Experiment(name) 
e.A1.append(b)
e.allchan(b)

then inside experiment.run():

for set in self.A1:
  self.bs.setup(channel)
  for g in set.bs.gainiter():
    for hpf in set.bs.gainiter():

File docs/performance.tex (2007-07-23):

\section{Performance}

\subsection{THD + N}
THD+N with and without input HPF filters, across gains

\subsection{RMS Voltage Noise }

\subsection{Noise Spectra} 

\subsection{CMRR}

CMR with and without input HPF.

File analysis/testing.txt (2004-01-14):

13 January 2004

Okay, this is the assembly and testing log of our (*pray*) final acquisition board. 

First, some last-minute component shopping:
25LC320/SN-ND		EEPROM
SJ5523-0-ND		Little rubber feet
399-1091-ND		extra bypass caps
399-1096-ND		extra bypass caps
67-1253-ND		RT < dual LED, red
240-1001-1-ND		big analog supply ferrite
240-1008-1-ND		smt ferrite bead
RR08P10.0KBCT-ND	precision 10k resistors

Now, testing plans:

one board, just analog stuff -- no digital

other board, just digial, no analog.

Things to test:
first, digital power supplies

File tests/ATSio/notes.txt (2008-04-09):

This is my attempt to make linux-GPIB do the right thing. 

This is using the NI GPIB card, with ni_pci_accel, and the tnt4882 module. 

FOR THE LOVE OF GOD REMEMBER TO RUN gpib_config

interface {
	minor = 0
	board_type = "ni_pci_accel"
	pad = 0
	sad = 0	
	master = yes
	timeout = T3s
}

device {
        minor = 0
        name = "ats2"
        pad = 1
        sad = 0

        eos = 0xa       /* EOS Byte */
        set-reos = no /* Terminate read if EOS */
        set-bin = no /* Compare EOS 8-bit */
}

ibtest can help

pad above shows that the device is on GPIB address 1

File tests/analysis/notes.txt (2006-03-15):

Notes for analysis. 

readraw: 

Returns a file object that will return the next N samples in an array when you call foo.read(N). 

Similarly, there will be readchan, which you invoke with 

x = readchan(filename, channelnum)

and will do the same. 

Oh, so we discover the IEEE papers on "coherent sampling" and similar
topics. Will now read. In particular, "Frequency Domain Testing of
ADCs" in the Spring, 1996 "IEEE Design & Test of Computer" (pp 64)
looks really good.

Also, there's an IEEE standard on testing ADCs 

--------------------------------------------------------------------
Reading and visualizing raw spike data
--------------------------------------------------------------------

We have:
extractTetrode(raw array of data, gain)

filterTetrode()

tetrode.spikes(threshold)

returns an array of spikes

clusterplot(spikes) -- six projections

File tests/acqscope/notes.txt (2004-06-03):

Quick attempt at making an oscope for the acquisition board. Try and use IO monitoring signal to update draw area. Draw area will be 10 ms:

5 ms * 32 samples/ms * 8x oversampling = 160 x 8 = 1280 pixels
or something. Need to see how it scales and all. 

Glib::RefPtr<Glib::IOChannel> ifile =
   Glib::IOChannel::create_from_file("testfifo", "r");
Glib::signal_io().connect(SigC::slot(*this, &ExampleApp::on_input_read),
                           ifile, Glib::IO_IN);

We have a double buffering scheme, bufferA and bufferB, each of points, and activebuffer, which is a pointer to one of the buffers, and bufpos, which is our current position inside of a buffer. 

Hmm, it almost seems that a better plan would be to have a big circular buffer foo, and we just read in data and update that buffer by adding on data to it. 

1. read in sample, save in buffer

    if pos < 0:
       if sample > thold :
          pos = 0;
    else
       pos++
       if pos == windowsize:
          copy previous n samples to window buffer
	  redraw buffer
	  pos = -1; 

Now, problems include intermediate redraws will perhaps see an incomplete buffer, but oh well. 

2. We'd like to add: 
   Code to show if we're in raw, normal, offset-disable, or fake-data mode
   code to let us switch between channels 
   somehow visually show, change threshold

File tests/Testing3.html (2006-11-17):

14 May 2006

Another day, another series of tests. Unfortunately, the acqboard prototype we received from eTech-WEB had numerous shorts in it, including an impossible-to-fix one that appeared to be under the PGA between channel B2 and B1. I have removed those channels for the time being.

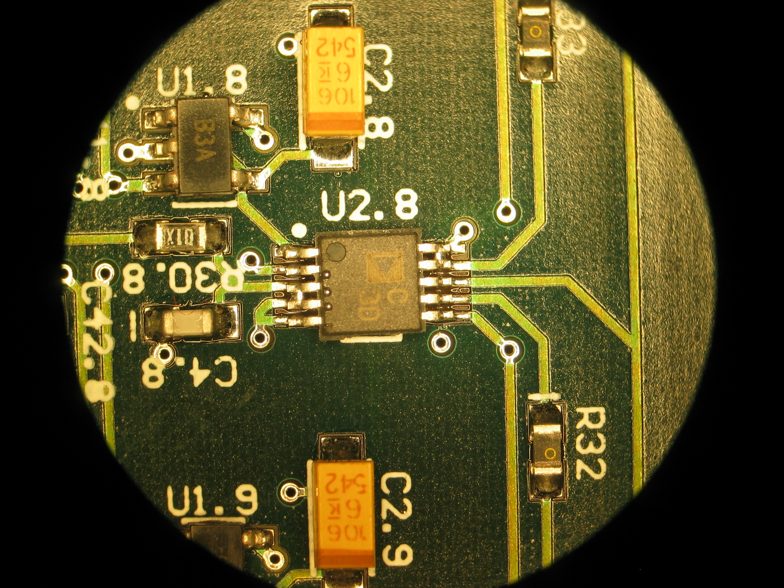
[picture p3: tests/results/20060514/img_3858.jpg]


The visible shorts on the ADC are above.

The current state of our benchmarking code really leaves something to be desired, and should undergo a comprehensive clean-up at some point in the near future. In particular, I'm unclear on how exactly I run THD+N tests, noise tests, linearity tests, etc. and produce my expected plots.

Ultimately, the problem is that the code that you want to run when debugging is different from the code that you want to run when running large-scale performance tests. The situation is similar with the graphical output.

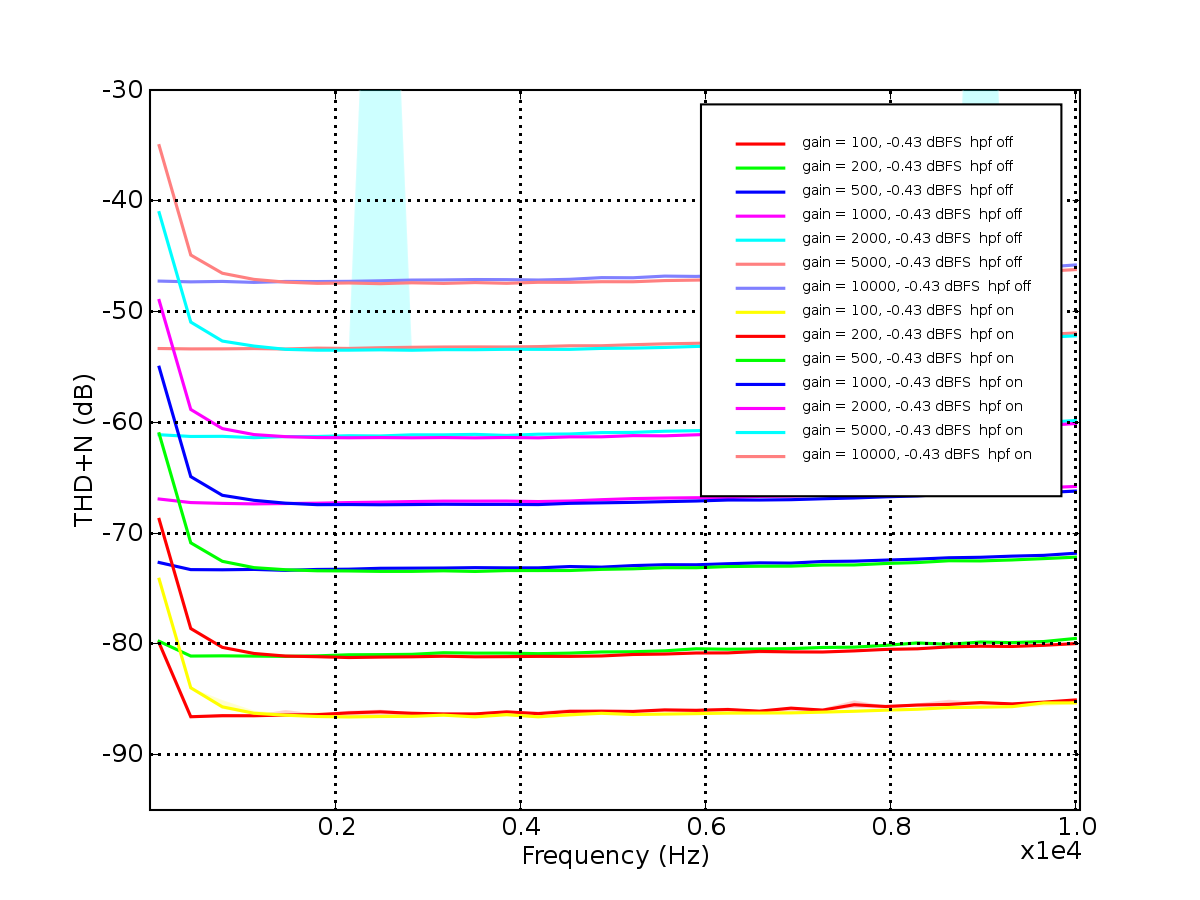
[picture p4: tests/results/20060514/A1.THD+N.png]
We generate the following data with Experiments2.py, and then use thdnMeasure.py to plot: 

Which is associated with the non-svn'd file 20060514.all.h5.

21 May 2006

Now we will attempt to verify performance across each of the acqboards. To do this I have written a simple "channel check" benchmark which tries to do a single full-scale THD+N measurement for all channels / gains / filter settings.

22 May 2006

6 of the acquisition boards appear to just work, but the seventh has some sort of ADC-related problem that has proven difficult to diagnose.

26 May 2006

We have 13 working acquisition boards assembled by eTech-WEB, and another 3 that need some sort of love.

1 June 2006

Board performance measurement for docs...

3 June 2006

Print-able noise benchmarks:

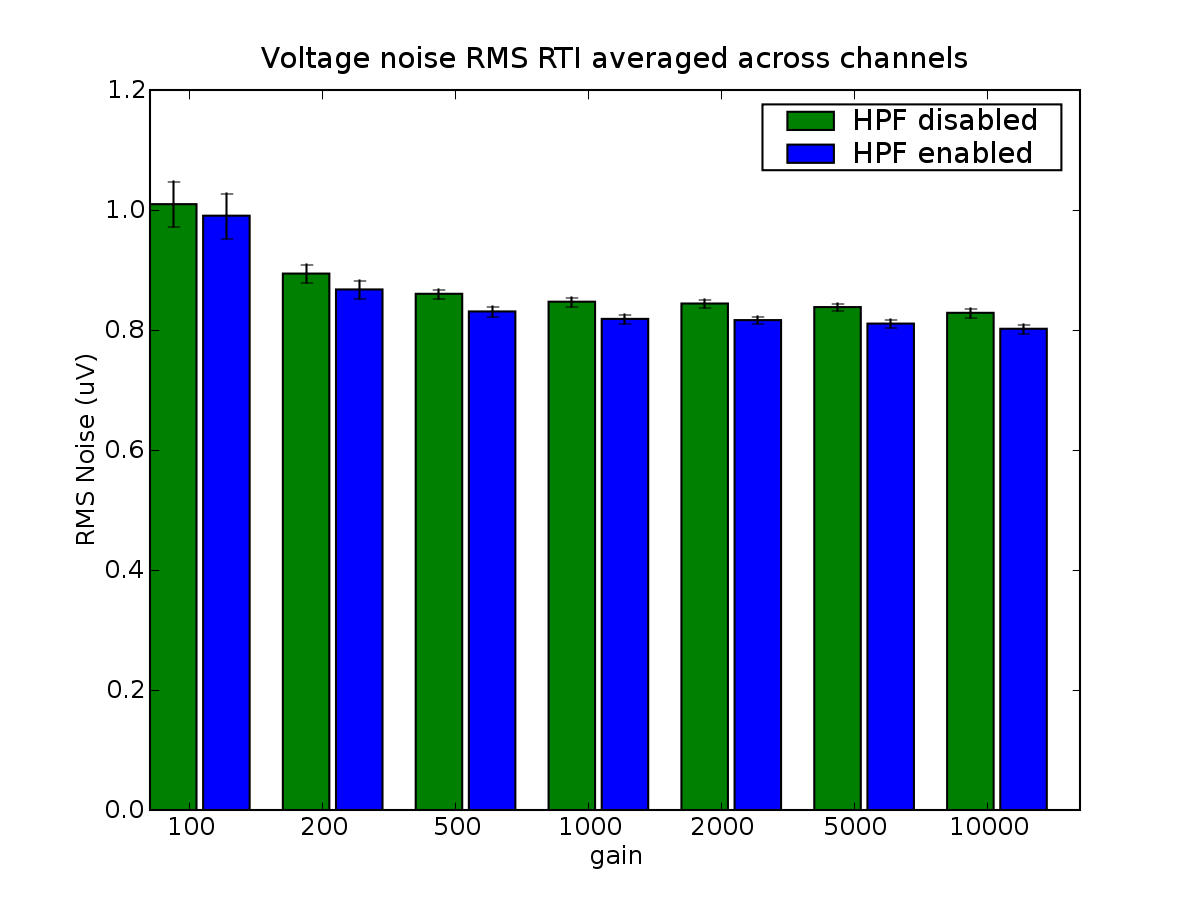
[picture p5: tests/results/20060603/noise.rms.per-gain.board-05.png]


Noise plot generated from no-svn/200606030-board.05.noise.h5 by averaging the RMS noise across all channels, per gain.



Of course, now I'm worrying our CMR might be total crap...

CMR Measurements:

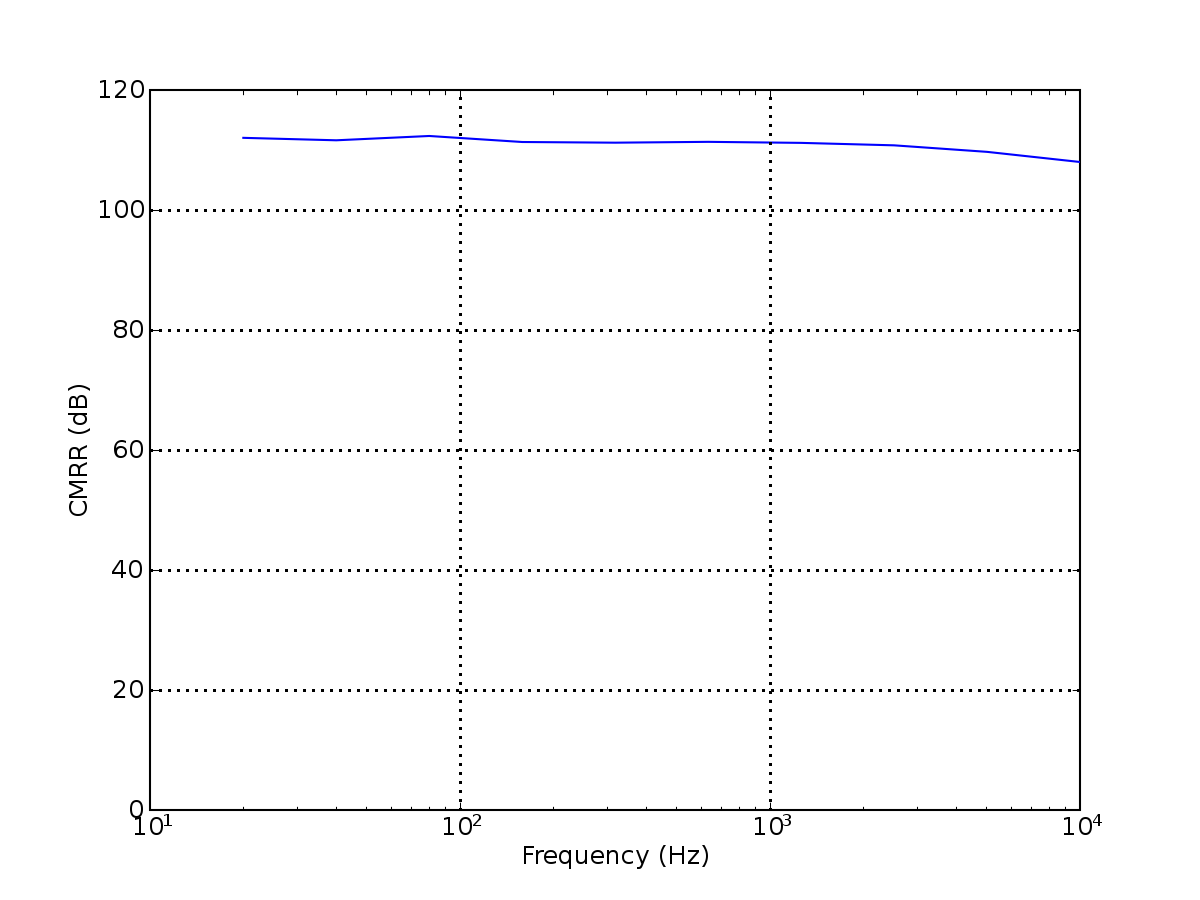
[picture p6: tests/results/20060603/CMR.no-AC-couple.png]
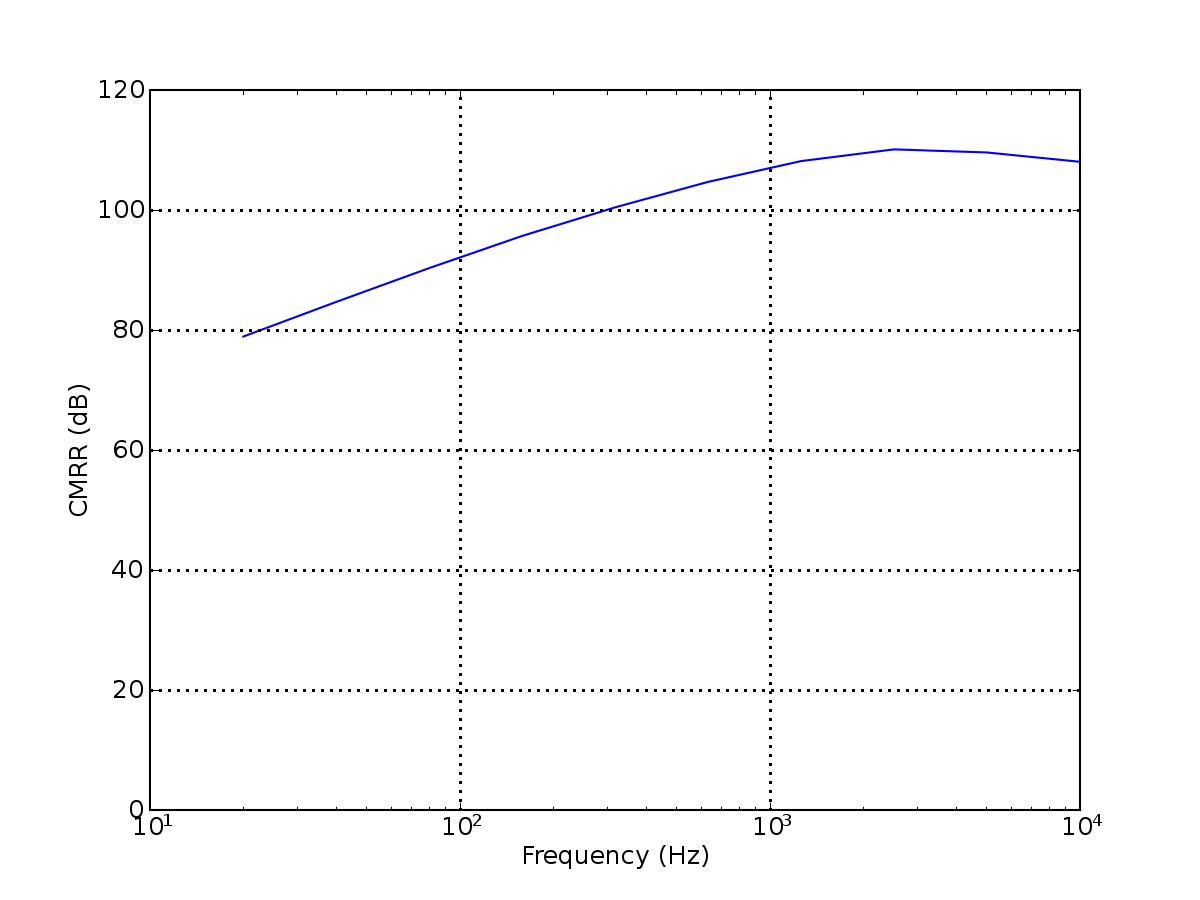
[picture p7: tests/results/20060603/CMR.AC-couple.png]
 | 
CMRR of board with AC-coupling hardware removed | CMRR of board as-shipping, with input AC-coupling HPF

As you can see from above, the addition of the 10uf/100k AC-coupling stage in front of the in-amps has significantly degraded our common-mode rejection, due to impedance mismatch between the filter elements. At high frequencies, this is less of a problem, and it still looks like we get ~90 dB CMR at 60 Hz, but it would be nice if we didn't have to take this hit.

Ultimately, the ramifications will depend on the measured CMR of the neuralynx amps, as a guide to how much CMR we "really need". Potential solutions would be:

- remove input AC-coupling, and perform the same thing at the preamp
- remove input AC-coupling, change in-amp gain to 10x, and reduce the ADC range by a factor of 10

Both of these can be done with our current hardware configuration.

Again, the above graphs can be found under no-svn/20060603-board.05.cmmr.h5

08 June 2006

Performance measurement, part two:

I want to measure the CMR for the neuralynx amp, and explain how part of what we're seeing is an artifact of the input AC-coupling filter.

As measured by the lynx-8 amp, we get:

with 5 vpp in and a gain of 10k:

freq | output Vpp
50 | 980 mV
100 | 980 mV
500 | 880 mV
1k | 1V
5k | 1v
10k | 960 mV

12 June 2006

Analog performance measure of the non-AC-coupled case:
1. noise
2. THD+N
3. CMR

Fabian suggested that I present it as "look, the THD+N curves are flat, i.e. there are no frequency-dependent distortion components, and the spacing shows that the primary contributor is the input noise."

Wow, so it turns out that part of our CMR problems were due to measuring the inputs shorted together. There's a lesson there, someplace.

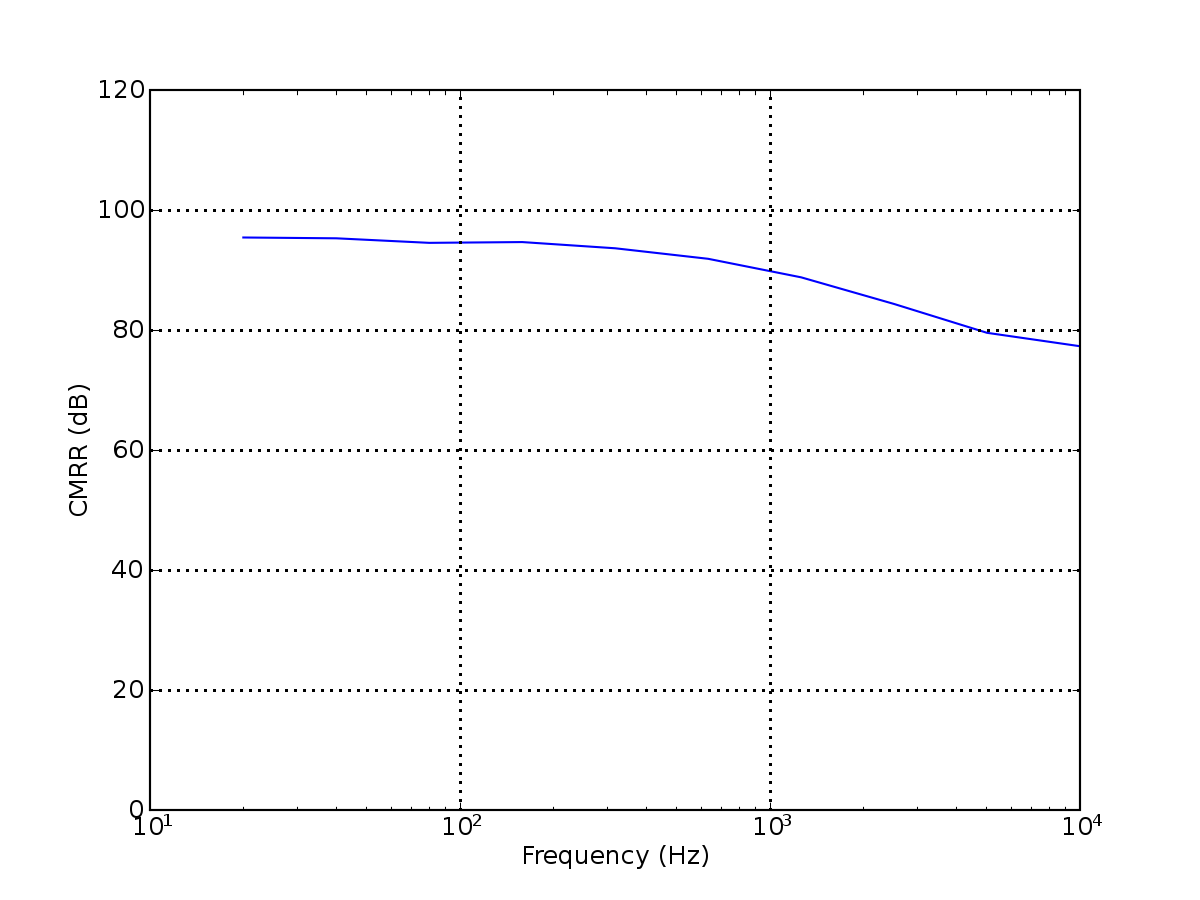
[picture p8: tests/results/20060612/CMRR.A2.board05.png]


Hmm, but if we measure the other channel, we get the original bad result. Ass.

We should check the precision of the resistors and caps we're using...

13 June 2006

It seems like the CMR consistently sucks. I'm going to build a new set of connectors, and buy some higher-end resistors and capacitors, in an attempt to track this down...

14 June 2006

After considerable effort, it appears we only used 1% resistors on the AC-coupling HPF; so I'm going to try and see if 0.1% resistors make things any better. In other news, MAD PROPs to BOMDB.

Unfortunately, they don't appear to; however, now I'm going to try with different classes of resistors as well.

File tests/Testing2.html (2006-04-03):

11 March 2006: Acqboard 01

Detailed test and assembly log for Acqboard 01: Digital side

1. First, we solder up the digital power
2. Solder QFp, etc
3. All back-of-board bypass caps are 0.1 uF Caps

Everyting soldered and documented; now try programming -- worked.

Now the analog side -- first isolators, then the power supply

Analog references appear to work properly.

We had to use non-recently-purchased 150 uf Caps, 311-1071-1-ND, CC0603JRNP09BN151 from digikey.

13 March 2006

Informal performance measurements of the ADC + AA look correct. Soldering on registers and the other hardware for further measurement.

With the ADCs, AAs, and PGAs, but without any earlier-stage muxes, and with the inputs all ganged together, we get :

Now, we solder on :
1. the rest of the channel's bypass caps
2. The Mux and amp
3. the 5.6k Resistor
4. We ordered the wrong 68nF caps, so we're jusing 490-3360-1-ND, a 1206 COG.

14 March 2006

Our results are as follows for the boards which have everything but the IN-A

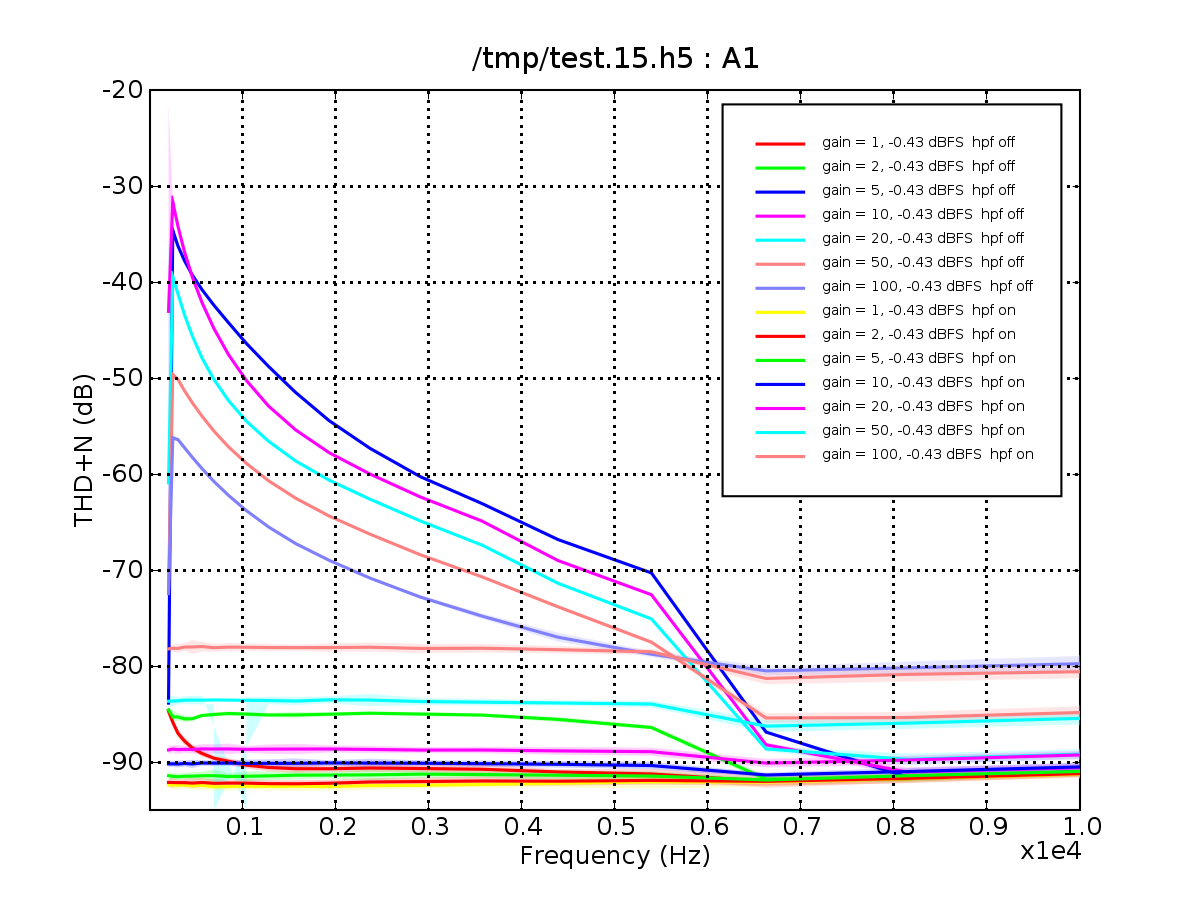
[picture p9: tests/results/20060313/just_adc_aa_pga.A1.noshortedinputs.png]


This is confusing and unfortunate.

Further refinement along the analysis end has show that, for high gains using the LPF, we end up with awful nonlinearities.

Below is the difference over serveral cycles between the recorded sine and the fit sine for a gain of 5 with the HPF enabled.

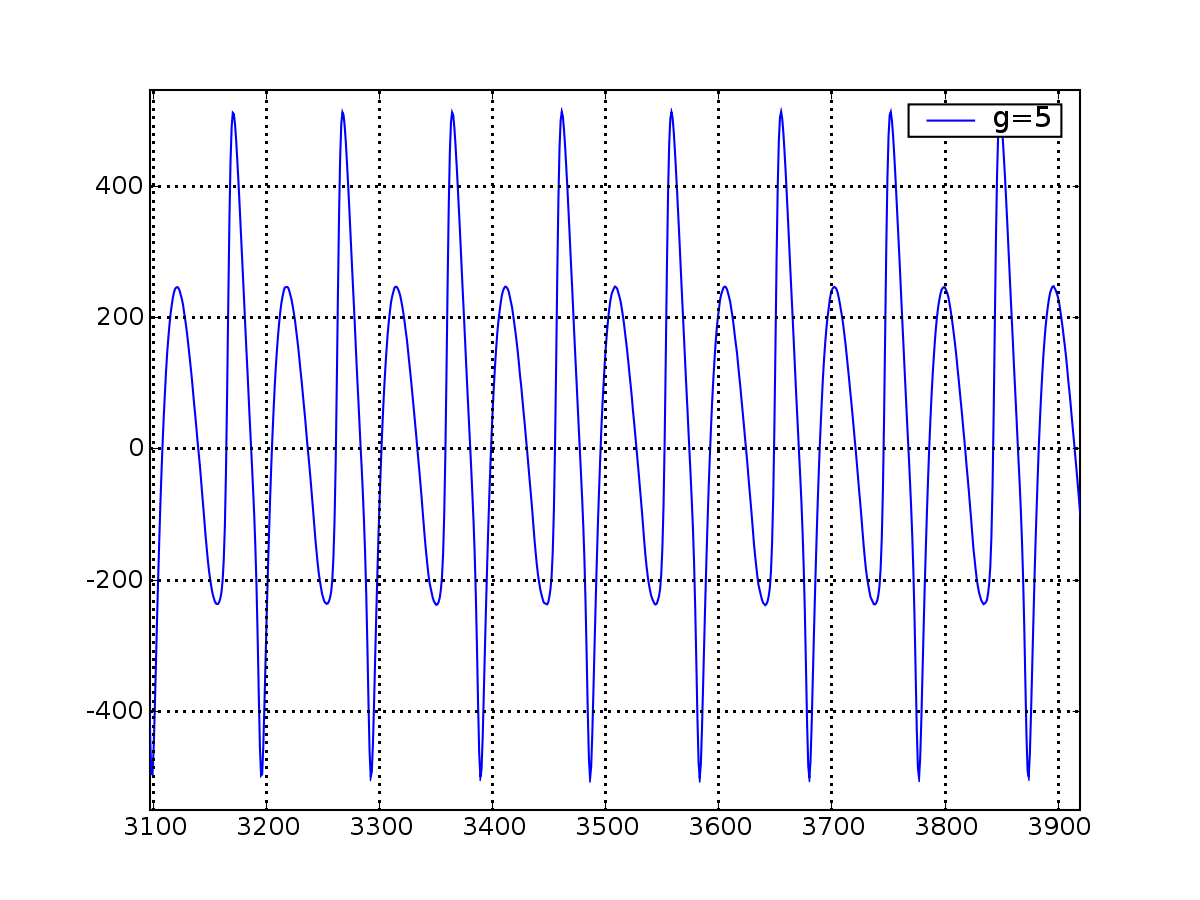
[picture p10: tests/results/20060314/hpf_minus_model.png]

I don't know what this is.

Resoldering the Mux appears to have fixed the problem:

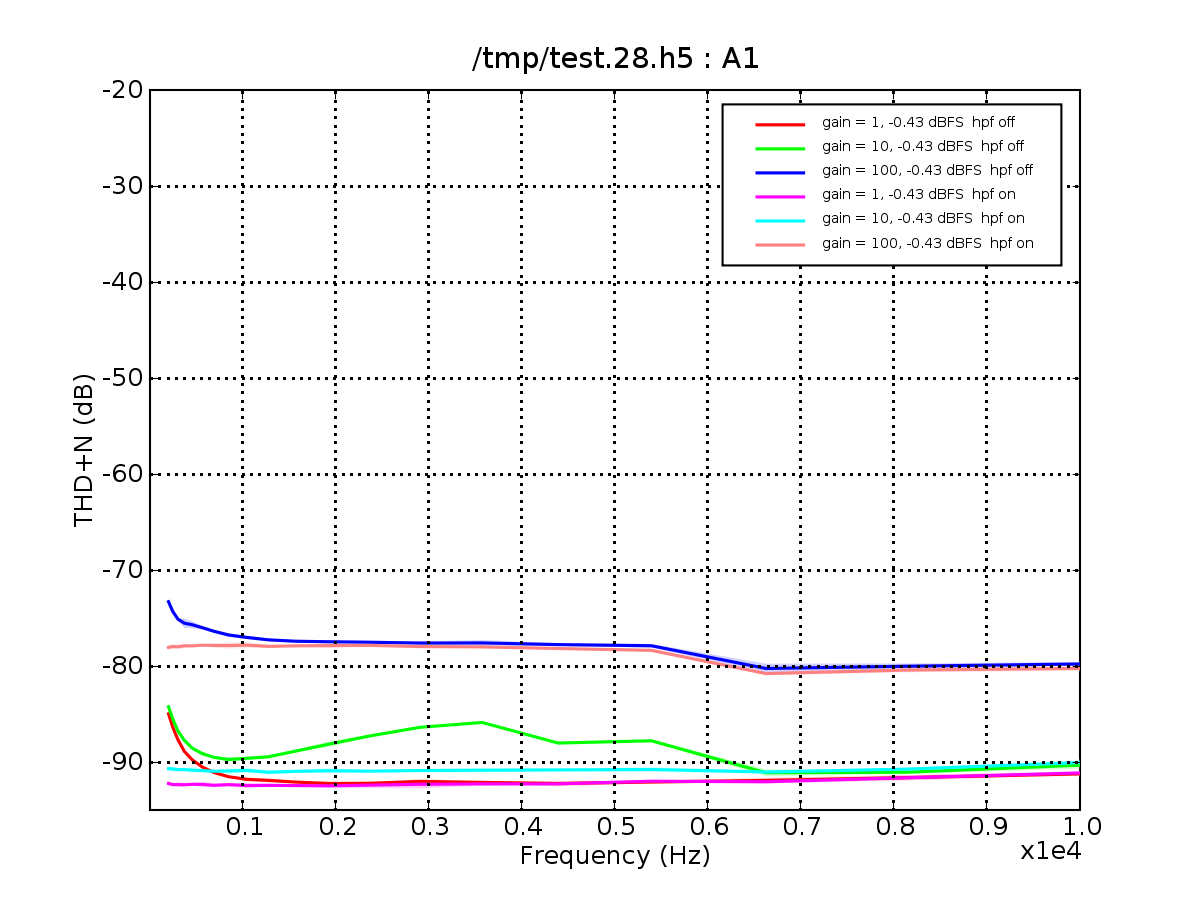
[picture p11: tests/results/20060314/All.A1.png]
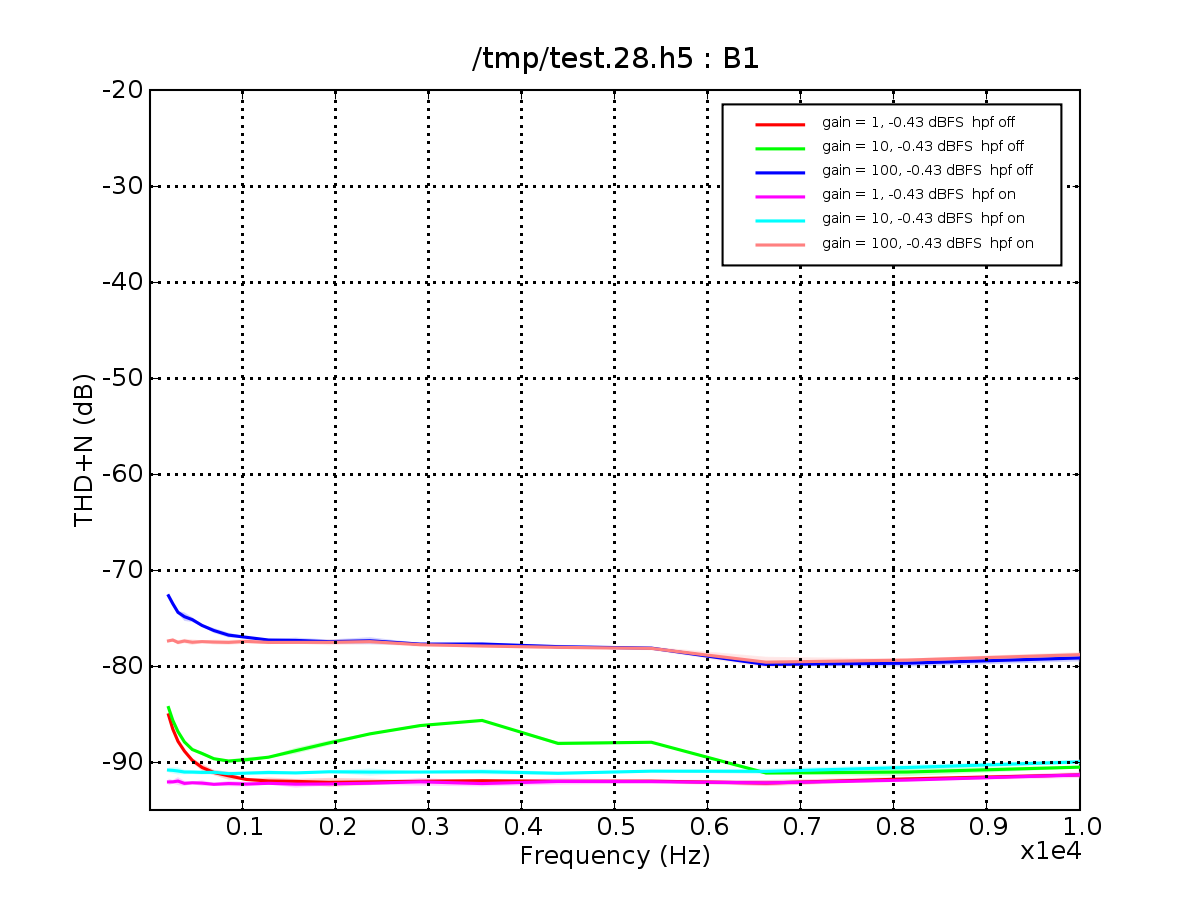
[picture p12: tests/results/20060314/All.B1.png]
 | 

15 March 2006
Now we try with the in-amps, AD8221AR. We use ERJ-3EKF1004V (P1.00MHCT-ND) resistors, 1 MOhm, and 1 uf Caps.

Things looked great, but now we're seeing a ton of non-HPF THD+N variance. To measure this, I've removed the mux and am just directly measuring the HPF-less signal chain.

Here is B1 initially, with an entire signal chain:


It looks great. The associated data is at B1.good.h5. (note this is with segnum = 100)

If we want we can seriously overdrive the ADC -- -1.8V to 4.2V!

This doesn't appear to cause any noticable difference, however, in the measured response.

Cleaned off the flux, now let's look... no real difference.

16 March 2006

Trying hard to be more rigorous here. It's not even obvious what we're measuring or how/why we should care. To that effect, I think that the current plots are not very useful/effective.

test.70.h5: Both channels A1 and B1 soldered; A1 Ac-coupling caps removed; using All-Chan connector.

17 March 2006
We continue, even after substantial refactoring of sine-fitting code, to get unfortunate-looking results.

As a test, first thing in the morning, we will record: Both channels A1 and B1 soldered; A1 Ac-coupling caps removed; using All-Chan connector.


Note that, contrary to what the graph says, the signals with high variance actually have the HPF -off-. I don't think what results is a problem with sine convergence, because we clearly have results -converging-, and there is a very clear difference between the HPF off-and-on states. This data is in early.B1.h5.

Test Plans -- to develop comprehensive testing, we're going to record noise data and sine data across HPF and LPF.

18 March 2006

I think it's more important to try and characterize the nature of our observed problem:
1. Is it real ?
2. why does it vary with segment size?
3. What is the spectral relation?

Here, we have the results of B1, gain = 100, hpf = 0, sine, a few sines.



THD+N for various frequencies across a series of frequencies.

There is more low-frequency noise in the hpf=off, so it makes sense that fitting over smaller windows would be tighter.

I'm going to try filtering the data and then seeing what we get.

 |  | 
THD+N across multiple segment sizes for 2.6k, gain = 100, with HPF on | THD+N across multiple segment sizes for 2.6k, gain = 100, with HPF on | THD+N across multiple segment sizes for 2.6k, gain = 100, with HPF on, filtered with

Note that when we (digitally) filter, we get a much flatter response (minus the edges, an artifact of filtering). And notice that the same thing happens when we reduce the segment size. My best conclusion is that we have some low-freqency noise (surprise!) that gets filtered out by the HPF, and that causes the problems we see in the LPF.

Given this, I think that the best future option will be fitting to short records. In addition, we will now specify our ns in terms of segment lengths.

19 March 2006

We need to robustly measure noise, and come up with a way of saving that data to the files that also have sine data.

Ultimately, we're interested in absolute noise at various gains.

 | 
Noise for A1 | Noise for B1

The channels start off with roughly the same amount of noise at G=100, but the noise stays flat across gains whereas B1 decreases.

This would seem to suggest ... A1 has some intrinsic noise, whereas with B1 the noise is ADC-dominated?

20 March 2006
Using the shorter THD+N windows, we get:

This would be fine except that we have really bad performance now on B1.

21 March 2006

At this point, A1 is the normal looking channel and B1, g=10k, hpf=off looks horrible.

We'll try power-cycling... no effect; now we'll try input B. No effect. What the hell happened?

So, to diagnose this we have removed the input AC-coupling network, and the 10 uF Coupling capacitor:



We get a graph that looks almost exactly like this when we remove the In-Amp and ground the input to the PGA/HPF subcircuit.

22 March 2006
TWe soldered on A3 and B3, without any part of the spike filter (HPF network -- no mux, no filter, no cap, etc.) and we get the following:


That is, A1 still has the bad performance, but all other channels appear to have ADC-dominated noise .

Accidentally ran against the noise tests, so we no doubt had some sustained periods of overvoltage. Let's see if that actually kills our THD+N.

23 March 2006

The THD+N we measure for these channels which lack the HPF circuitry or AC-coupling is:

 | 

111, 112 are new with AC-coupling:

 | 

Wow, A3 looks like total shit. But noise measurements show that A3 and B3 still have good noise performance.

Now, to check, we'll replace the AC-coupling components on A3 with just the zero-ohm resistor -- we clearly get the same A3 as above.

What is up with the upper side of the board? We've removed mux and HPF amp from A1, and resoldered AC-coupling r/c on A3, and will test again -- we still get the same poor non-flat response for A3:


Now, with a different XLR-connector board (one which also provides input to A1's current no-AC-coupling In-amp) we get something that looks virtually identical.

24 March 2006

As best I can tell, an artifact of adding the AC-coupling components is to generate very-low-frequency artifacts which impact THD+N.

Let's try with 1M/1uf vs 100k/10uF:

 | 
1 MOhm, 1 uF | 100k, 10 uF

Now, let's measure our noise perf:



The B3 channel shows exactly the same performance when we substitute resistors like this.

Now, we add on other resistors and use the multiple-input selection; what happens when the input is loaded down by multiple resistors? We don't really care, but...

Now, we've soldered onto A3 and B3 the HPF-amp and the mux, but not the R/C; now let's measure:

 | 

As near as we can tell, the above are complete channels.

Oh my, there are horrible systemic errors in all of the previous NOISE MEASUREMENTS.

25 March 2006
Let's try and measure noise properly now...


Okay, that looks pretty awesome.

27 March 2006

Looking at the results after a few days, and a board cleaning: Looks fine. A3 and B3 have good THD+N.

29 March 2006

All of the channels that use the old HPF caps have the strange THD+N curves; the current ones don't. It is very possible that 490-3360-1-ND is the solution to our problems on that front.

Noise performance looks great across all channels -except- for A1, which has its long-standing problems.

31 March 2006

So here we are:

 |  |  | 

Apparently a large part of the crappy results arose from our choice of the HPF cap -- the answer appears to be GRM31C5C1H683JA01L, or Digikey 490-3360-1-ND.

WE've confirmed that the noise in a neuralynx amp at g=400 = 5.7 uV RMS, and g=40000 are 3.9 uV RMS.

SOldering up A1, we note that the AD8510ARMs in the box are marked differently from the ones in our package. We are using the box one for A1.

Still, performance on A 1 looks great.



Noise performance. Woohoo, spring break!

1 April 2006

There exist many situations where csinlesq will return one result and pysinlesq will return another, and this is very frustrating; sometimes these differ by as much as 90 dB! It seems that all the poor-THD+N results were essentially artifacts.

Also, simply shorting A1 and AC doesn't appear to negatively impact either; now we'll try with in-muxes

2 April 2006
Unfortunately, the performance on the inmux channels looks awful.


I think this is a direct result of the large voltage swing encountering the non-flat RON; to test this, I'm going to replace the AC HPF with a zero-ohm resistor and then remove the PGAIN pin. Thus the input to the mux (U9) will be through a AD8510 ARM buffer.

3 April 2006

I think we're ready to go. Although oh my, I may have been calculating noise wrong this entire time!



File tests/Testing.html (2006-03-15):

13 January 2004

Okay, this is the assembly and testing log of our (*pray*) final acquisition board.

First, some last-minute component shopping:
25LC320/SN-ND EEPROM
SJ5523-0-ND Little rubber feet
399-1091-ND extra bypass caps
399-1096-ND extra bypass caps
67-1253-ND RT < dual LED, red
240-1001-1-ND big analog supply ferrite
240-1008-1-ND smt ferrite bead
RR08P10.0KBCT-ND precision 10k resistors

Now, testing plans:

one board, just analog stuff -- no digital

other board, just digial, no analog.

Things to test:
first, digital power supplies

14 January 2004
Okay, there's already some code in the "vhdl" subdirectory. Today, I'm going to create LEDFLASH.vhd which will just flash the leds to let us know things have booted correctly.

Baah! After all this work, the vias on the lower right side of the board didn't connect to the plane! I don't know why -- did I send them the wrong gerbers? Is this a power plane issue? WTF?

9 Februrary 2004
After working on the DSP board and getting it + it's accompanying FPGA code mostly done, we can return our focus to the Acqboard, the make-or-break component of the system.

First, Analog power system, which appears to work.

Just the output of the AD8221, nothing else. Just A1.

So, first, just going to solder up an AD8221 and see what we get.
Please note that board 1 Channel A1 is using a 1.0% 475-ohm gain resistor that measures 476 ohms.

23 February 2004
We get what looks to be 150 uV P-P noise when shorting the inputs of the A1 AD221 together, at g=104, would translate into < 2 uV input noise. Strangely, it also looks like we've got a roughly 1.5 uV input Vos, which seems low.

16 March 2004
Updated filter design
corrected values to make second-stage 2nd-order LPF bessel with correct
values

verified in SPICE

15 April 2004
isolators + shift registers appear to produce correct outputs for at least a subset of the outputs (i.e. didn't test all)

17 April 2004
Discovered that the wrong packaging was used for the EEPROM -- TSSOP and SOIC packages have different pinouts, and was using the TSSOP pinout withthe SOIC package. Obviously, this won't work. Solved by removing IC, soldering CS\ and SO pins together, so all values read should be zero. This will prevent testing EEPROM reading, writing, on this version of the acqboard, and will require us having loaden == 0. Which sucks. But it will still let us measure a great deal of analog performance.

23 May 2004
Getting ready for tomorrow's testing and assembly.

24 May 2004
Well, look who didn't remember to update the overlays. This really sucks. So, pending the arrival of the jtag hardware today, we'll test to make sure we can boot, but that's about it.

Things wrong on the acqboard:
Overlay text overlays some of the traces.
The connector size for the jtag programmer is wrong.

But, using 5k Ohm pullups for all pullups and 200 ohm current-limiting resistors, we have things working. We can connect to the chain, program the PROM, directly download via the jtag chain to the FPGA. I'd say this jtag setup was a success.

30 May 2004
A short between VSS and GND on the analog side caused this board to be a loss, but luckily I was able to test the DL capabilities, and sure enough, the acqboard command interface appears to work correctly. However, the code is fragile for a number of reasons, including (but not limited to)

3 June 2004
Can successfully download, boot, read filters, sample buffer from EEPROM, acqboard. Turns out there were problems with which exact bytes we were reading with the loader. Note EEPROM needs you to wait the FULL 5 MS before you try another operation following a write.

Mode 2 will only use channels 0, 4, and 8 for the sample buffer due to the way in which we write them.

17 June 2004
So, the new connector size is correct, but the connectors we bought don't have the correct notch and so in general don't fit. But the bigger issue was that the solder mask expansion on the connector wasn't large enough, thus scraping ,and the hole's werent' big enough, hence drilling. The problem was the VCC and the GND connectors, which needed jumpers.

AS of now, things are booting.

18 June 2004
Wow, mixed up OVDD and OGND pins on ADCs. I suck.

1 July 2004
We can get sine data in raw mode. Now, I'm not sure why everything else isn't working, and I'm also not sure why we evidently have this damn jitter, but I'm going to write some analysis code today to look at it.

2 July 2004
Switching the inputs on the INPUT stage for A & B, such that things will behave like I expect them to.

10 July 2004
Today we begin writing the batch data collection code... we'll see if this really works!

14 July 2004

Initial tests show the second harmonic to be down by only 60 dB; I'm not sure what's causing it, but I've devised a plan to check. We're switching the test write-up to HTML and we're storing all data in HDF5.

The format will be as follows. We're doing all of this with pytables (http://pytables.sf.net) as a really nice interface. Lovely, though, it appears pytables doesn't support storing of arrays as attributes (metadata). So we use... strings!!!

All files will have a "notes". We can also attach notes to each channel.

each file will have a channelname (A1, AC, etc) off the root, which will be the data for that channel. In general, then, a file might have:

/A1/sine/run0
/A1/sine/run1
/A2/noise/run0
/A2/noise/run1
/BC/IMD/run0
/B1/real/run0

The root will always have a "notes" field, as well as

now, each "run" has the necessary metadata to fully describe both the state of the acqboard and the function generator:
Function generator:

amplitude tuple of 2 floats (for IMD)
frequency tuple of 2 floats (for IMD)
mode (any of the noted modes, 0=sin, 1=sqr 2=white, 3=pink, 4=2tone)
offset (float)

Aqboard:
mode (int)
inchanA
inchanB
gains = tuple of 10 ints, as string
hpfs = tuple of 10 ints, as string
rawchan : raw channel

Now, how to organize the code?

Ideally, we do:
create acqstate object
create fstate object
perform run, take data
save as "location", acqstate, fstate

really, all this code should live under "analysis"

"test" handles interfacing with all the components and retrieving the results

"run" will handle putting the data in the relevant format for hdf5, saving the results, etc.

How to organize "runs"? what we really want is something that will just DTRT given an acqstate and a function state, and a number of samples.

So, a "run" could be a hdf5 wrap of a test. That wouldn't suck.

15 July 2004
First, we want to run the pure sine test, using a coherently sampled sine wave. Early tests suggest that we're not getting quite what we'd hope for... so we've created this notion of "sets" of runs.

Generated results/20040715/simplerun.h5 sweeping through gains, freqencies on the first ADC, both inputs.


The above is the result of channel A1 being fed a 207 Hz coherently-sampled sine, using a gain of 1 with DC-based HPF. Similarly,

This isnt' the best way of visualizing this, I think I'm going to write the "show" code to write parameters...

Anywho, the results look similar across the board -- 76-77 dB of actual SNR.

Now, let's look at raw noise.

The noise data is truly bizzare. All of what follows is from rtinoise.h5. We get as-expected noise distributions for low gains on channel A1:

   

So, visually, the distributions for the high-gain outputs looks really poor. I have no idea where the spiking is coming from, although there are a few candidates:

- external environment noise. Okay, maybe, but why the unusual distribution? The spikes appear truly random in time, but clearly quantized in amplitude.
- They could potentially be bit-errors in the readout. But they show up in powers of two. For example:



So hmm, that doesn't look suspicious?? But even if you assume errors in bits 7 & 8, WHY those bits and WHY only at high gains? This does not make sense, at all! Perhaps the errors only manifest themselves when the input is in that region? It can't be an 8b/10b related issue, because that's a byte-encoding. The input-range hypothesis can be tested.

So, could we potentially have an error -any- place we have a 16-bit interface?

Wow, looking back, this is the histogram for the diff for the A1 channel with freq 1 at g=100 with 100% amplitude:



The red bars are at +-256 and +/- 512. Wow, wow, Wow.

An interesting idea would be to see what we can get out of the simulated output mode. Inital inspections suggest nothing; maybe we only get errors for certain ranges? Let's program the sample buffer for a 0-255 sweep...

Well, after investigating a bit more, there is some sever strangeness occuring with the sample buffer mode. I don't quite understand what's going on. In any case, that's a day!!

16 July 2004
Now, it seems that the sample input is having problems -- let's see what's up!

THE OUTPUT VALUES GO FROM 0 to 248 BECAUSE IT IS DOWNSAMPLING THE OUTPUT! YOU FOOL!

When we run with a random sequence of inputs, we don't have problems -- we read out a reasonably random range between -32768 and 32768, without error.

The thing is, this just -really- looks like an ADC problem -- I can't think of anything else it might be!

Channel modifications

- A3 has connected the output of the inamp to the input of the AA filter
- A4 is shorts the input of the AA filter to nearby ground

So, we're still getting the noise problems (see results/date/rtinoise.modified), so we took the board and resoldered around the ADC. One pin on the A1/2 ADC wasn't soldered correctly.

So, having soldered, now we'll take more data. And we get outputs (from results/data/rtinoise.modified.post-solder) like:



Which, umm, is crap. Look at that!!! Smilarly, for A1:


So, here we are, the same place we were yesterday, but with more inputs. I really have no freaking idea what to do.

While out at dinner, came up with a few small ideas. First, per-bit statistics: mean, variance, distribution.

Bit statistics appear to tell us nothing unusual. But look at this:

 This is a histogram of the differences from the full record of A2. Wow, it sure does look like, say, 255 is getting randomly added or subtracted there!! But where? where is this coming from? ADC errors?

Even on the sine data! Here's yesterday's sine recording, but a plot of the diff() of the signal!



Again, how horrible!! We're running out of potential candidates. Now, it -could- be a problem internal to the FPGA, but that's just so unlikely that I'm not even going to consider it. Although the above suggests either an -amplitude- or -phase- correlation. But rather than hyper-analyzing it, let's figure out our timings again. The only plausable candidate at the moment is the isolators, although I'll be damned if I can figure out how they'd cause -this- sort of error.

Measuring on the scope, a SDOUT bit width is ~50 ns, which, when you sum the worst-case propagation times for the various components in the chain, "might" be an issue. Except that measuring the propagation delays of various bits of the system with the scope suggests that we're really looking at a P(delay) of, oh, 10 ns -total-. The ADC seems to be pretty good at sticking with 2 ns. At the same time, the sorts of single-bit errors (why always the same place) suggests a real fundamental problem.

On a slight hunch (yikes!) I'm going to try and sample one cycle earlier.

Umm, that appears to have made things worse! Sampling one cycle sooner (INCE one cycle ahead) gives...


At least this strongly suggests what the real problem is. The downside is how to work around it -- how can we possibly hope to speed things up at all?

17 July 2004

Okay, new day, new calculations. Currently we allow for 139 ticks (2.17 us) between CONVST assertion and when we start reading. That's way too long. Really, we could go to 112 ticks and be fine. Maybe even 120 to compensate for propagation delay. Alas, even after adding the extra cycle, we're still getting the same errors, although perhaps the DL to the board didn't go correctly?

So we reverted to the original input code and made a simulation of the inputs.. no problems. Ass. Even when we have raw mode disable the offsets, we're still getting the errors.

Simulations seem to suggest that we can endure aggregate propagation delays of 44 ns between when we actually output SCLK and when we get the result.

There appears to be a dependence on the amplitude here.

Rapidly running out of ideas, fish found some unsoldered bypass caps and soldered them, with no result. Similarly, I've changed the ADCIN inputs on the FPGA to use internal pull-downs. Again, no luck. What about a pull-down on the analog side of the IO converter? Still no difference. At this point, I'm willing to say that the sticky bits hypothesis has no real luck of going anywhere.

Okay, there are two types of problems: those I can fix and those I can't. Those I can't fix fall into

- Something wrong with the ADC:
  - it just sucks, and you're SOL
  - There's some problem related to the reference
  - there's some problem related to the internal converter
  - there's some problem related to the input
- Something's wrong with the GMR Isolators
  - You just can't drive them this way, i.e. they get stuck sometimes and there's just nothing you can do about it

Moving INEN to the SCLKH1 line hasn't accomplished anything... I feel like I'm going about this all wrong...

When I intentionally read too few bits, I get the following from channel A1:

This, while pretty, is -not- what we're getting, although it -does- look somewhat familiar. A2 looks near-identical. Frustration, coupled with near-insanity, is forcing me to ditch the output registers, and just focus on a simple interface with no output registers. Yea, we could have glitches on the output (although how likely is this?) but ... it simplifies things tremendously.

SCLK out of FPGA | 4 ns
cross 1st ISO | 15 ns
SCLK to SDOUT | 18 ns
cross second ISO | 18 ns
into FPGA | 4 ns
setup | 2 ns
TOTAL | 61 ns

For comparison, the full 4 cycle setup will take... 62.5 ns!!!

WEll, I re-wrote the input code for the ADCs, taking out the pipelining (but also removing some of the registering -- whatever) and I'm excited that I can hopefully eliminate it as a potential issue. But still... same errors.

18 July 2004
Wow, rapidly running out of ideas. The fixed ADC code hasn't helped any. I still get the quantization, even when I directly connect the unbalanced output of the function generator into the input of the ADC.

Watching the output on the scope, we can see that all output values are being set. This can be seen by triggering off of CS and taking the average; any stuck value would be apparent. We see the same thing on the other side of the FPGA. Even having the FPGA latch bits suggests -- there's no bit sticking!

In an attempt to re-evaluate where we are, I'm going to re-acquire a sample.

Indeed, results/today/sineagain.h5 shows A1.g100.f1.a100 to be nearly the same as above, with the same problems. Let's look at the hist of the diffs...

 

Now, the diff histogram is similar to earlier (pre- New Input.vhd) data, but the odd multiples of 8 never showing up as diffs is totally an error.

Interestingly, A3 & A4 don't have this problem -- maybe it has to do with the pull-up resistor? Cutting resistor and rerunning...

Nope, still the same problem. Here's a bit-plot:


This is for A1, g=100, data taken from sine_noresistor.h5. Both A1 and A2 exhibit this problem, but A3 does not. But the shifted outputs of the ADC (as measured by averaging) don't appear to have this problem! In fact, both bits 2 and 3 appear to be unaffected. This is now super-duper odd, esp. since it only affects ADC1.

Went down, made timing constraints a bit tighter on CLK, and switched all input voltage levels to LVTTL. Didn't help with -either- problem; A1/2 still shows identical bits 2 & 3; both ADCs 1 & 2 still have 256 problems.

Now we get desperate: we're going to trash the input stage. Make it as simple as possible; all we'll get out is the input of chan 0

Then I tried to totally rewrite the input code to just do a quick hack, but I -still- get the 256 errors. BUT that fixed the 2/3 bit stick error. Grrr.

This does not make sense.

19 July 2004

Okay, I want to sample this, and I want to trust the results. I wanted to write an interface to the oscope, but both it and the 6.111 Lab analyzers have too shallow of memory depth.

The people at analog devices are being helpful, and I'm preparing some code histograms for them.

20 July 2004
Sent things to Analog, waiting for response.

13 August 2004

Many responses from analog engineer; in particular, we'll want to buffer the reference input to each ADC. To test and see if indeed the reference was the problem, I desoldered the resistors to REF pins on the ADCs, thus disconnecting all ADCs from the input reference; I then shorted across this resistor for ADC1 and took data on A1.


This is really depressing. Chris suggested that I consider the problem is still the FPGA, and look at the converter output bits using a simple precision DC source. We really haven't tried this option, and it's worth a shot. I just need a precision OA and some resistors...

15 August 2004
I built the precision DC source, although I may have subsequently burnt it out. No bother, though, because ADC4 appears to have difficulty reading even bits:


What to do, what to do...

16 August 2004

Okay, accepting the fact that we obviously have some digital signal integrity problems here, how can we rectify these?

Well, my first zeroth-order guess as to the problem is that it's some sort of timing-related error in the FPGA. While I know that EVERY SINGLE FPGA-based error assumption I've ever made has turned out to be really really wrong, I'm going to still try to replace the input side.

Having lobotomized the input stage, we no longer have the no-even-values error. This means that the digital input portion of the FPGA was at least partly responsible. So, we'll have to fix that.

But, that said, for some values of the ADC input, we get a really nice output. For other values, generated from our DC source, we get:

 

With the actual value histogram on the left and the diff histogram on the right.
When we take the output of the ADC, in averaging mode, for channel B (thus the first 16 bits we see there) we get

 Note then that the low bits are -all- being triggered; this suggests some really fundamental signal integrity problems.

At the same time, the following is the histogram from the input shorted to ground:



This really suggests the ADC is sucking for some number of reasons.

24 September 2004: The Analog Test Board
The availability of the awesome Audio Precision ATS-2 for measurement has prompted me to build an analog test board, which will let me measure all aspects of the analog performance, including a comparison of three different op-amp AA filter designs.

We've built the discrete AA filters using a 4-stage (8 pole) MFB architecture, and used TI's FilterPro to select component values. Now, I'm a bit confused by this FilterPro program, as it renders different stages differently, but it claims to work well. Ha. In any case, the Bessel MFB 8-pole with a 16.5 kHz cuttoff and a 10k seed resistor (with E24 resistors and E6 caps) gives us -95 dB at 128 kHz while having only -1.1 dB at 10 kHz. Booya.

In some sort of sick conspiracy, I designed the board with the AD8513ARU instead of the AR, and now I get to wait for a shipment of them from digikey. Wow, I'm sure glad money isn't much of a constraint.

26 September 2004 : Analog test board results via ATS-2
The output of the ATS-2 is interesting; it is a fantastically complex instrument, or moreso, it does some complex DSP. Really, all I want is something that costs $10k and takes in / puts out the desired signal leves so I can do my own fucking DSP. But whatever.

The device calculates THD via an FFT (by summing the harmonics) and a THD+N by the standard notch filter approach. This is important to recognize when trying to calculate and compare these sorts of numbers.
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

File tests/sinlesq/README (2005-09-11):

Code to perform IEEE-1057-1994 sine fitting

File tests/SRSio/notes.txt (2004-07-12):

Python interface to the Stanford Research Systems DS360 digital function generator via serial interface. 

Ohh, pyserial appears not to suck. That's good.
python setup.py install --home=/home/jonas/python
or apt-get install python-serial

stty -a -F /dev/ttyS0

We'll have a simple interface:

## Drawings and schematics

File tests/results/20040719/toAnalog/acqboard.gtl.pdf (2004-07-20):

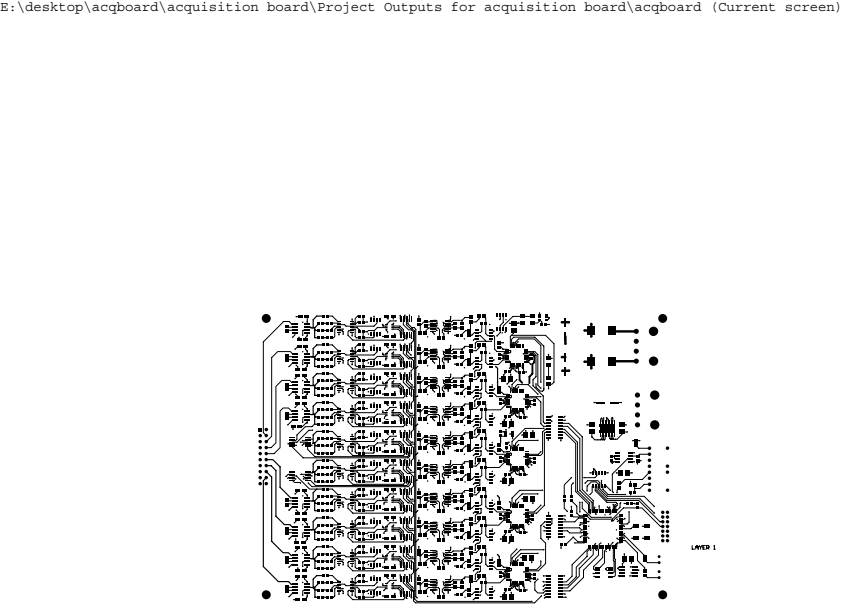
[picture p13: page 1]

E:\desktop\acqboard\acquisition board\Project Outputs for acquisition board\acqboard (Current screen)

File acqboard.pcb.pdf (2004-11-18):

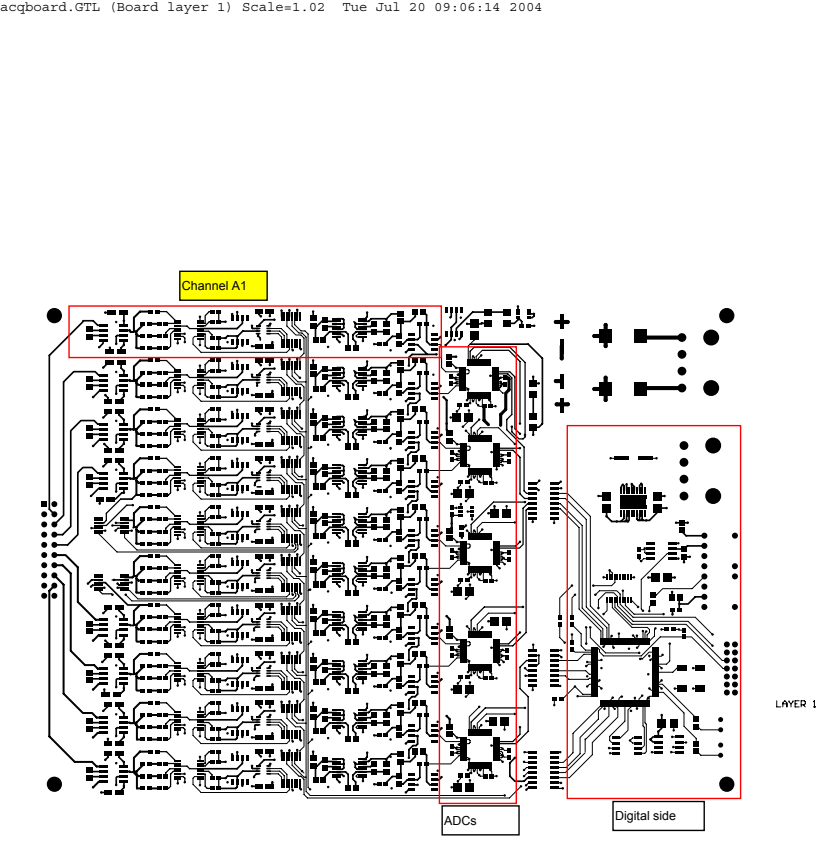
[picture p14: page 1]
acqboard.GTL (Board layer 1) Scale=1.02; Tue Jul 20 09:06:14 2004

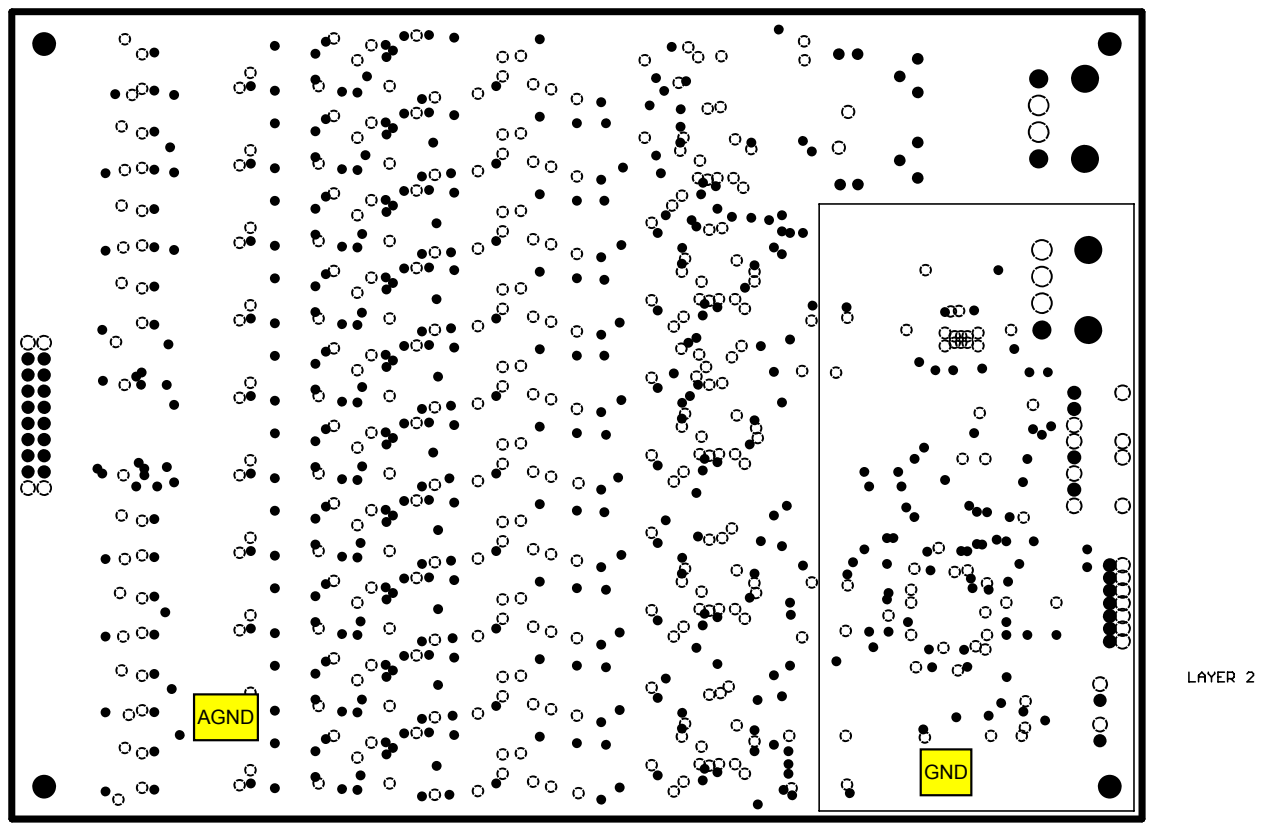
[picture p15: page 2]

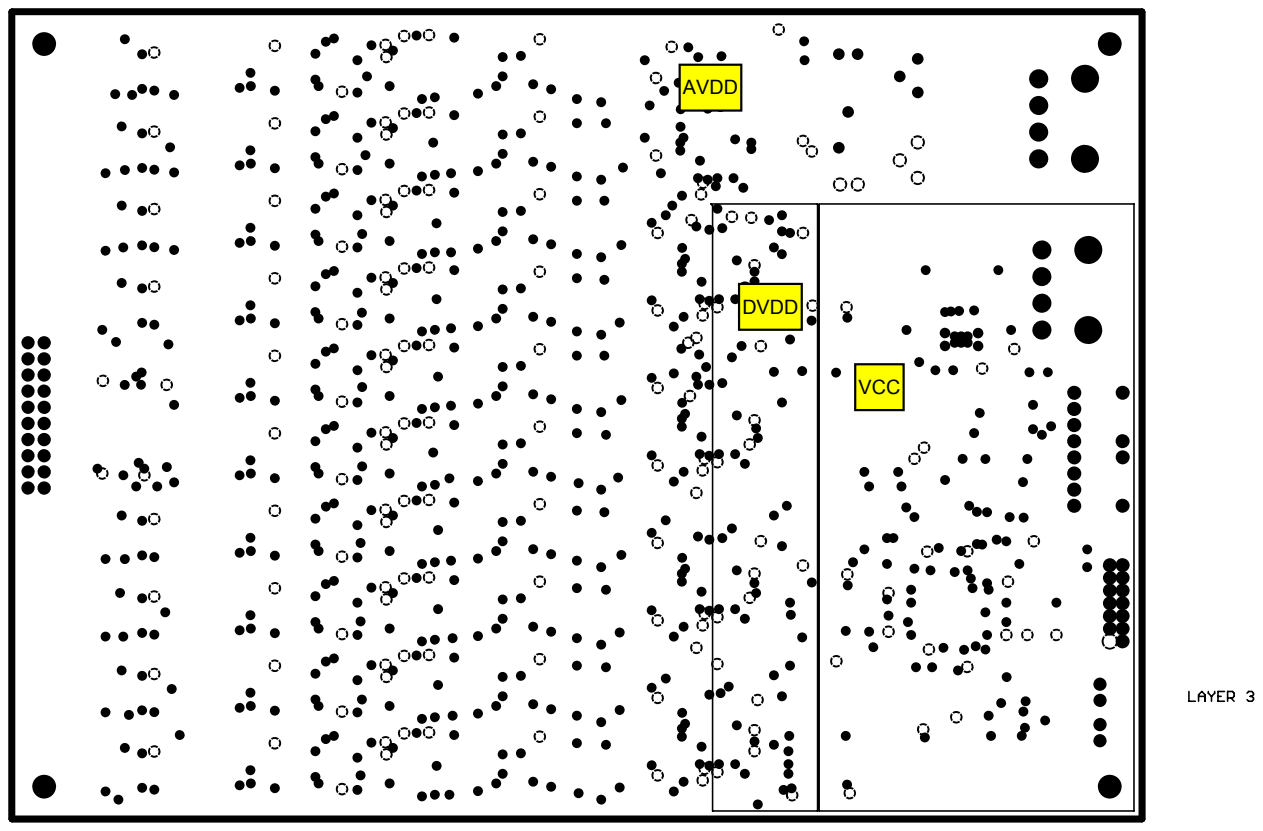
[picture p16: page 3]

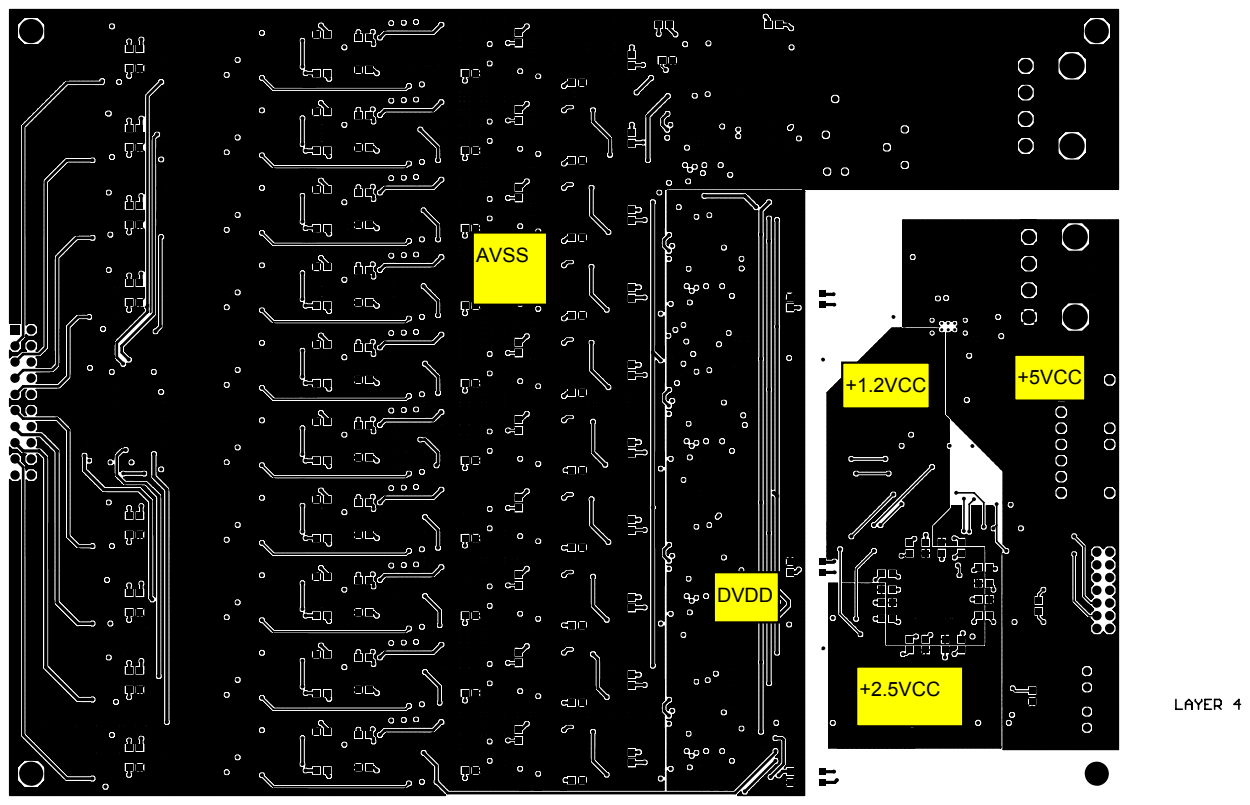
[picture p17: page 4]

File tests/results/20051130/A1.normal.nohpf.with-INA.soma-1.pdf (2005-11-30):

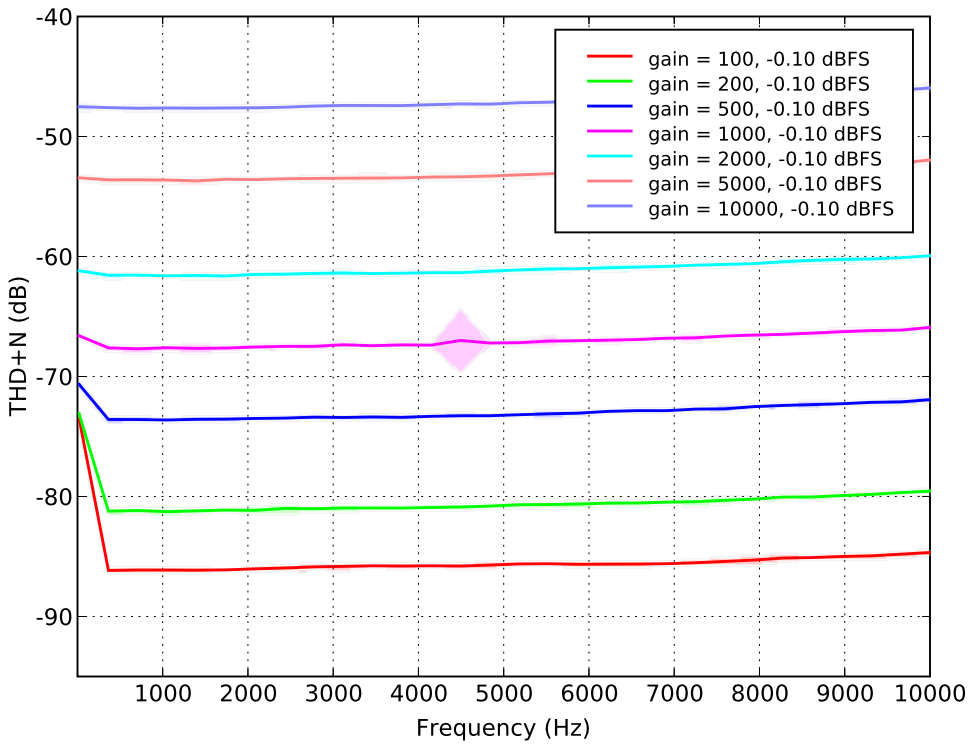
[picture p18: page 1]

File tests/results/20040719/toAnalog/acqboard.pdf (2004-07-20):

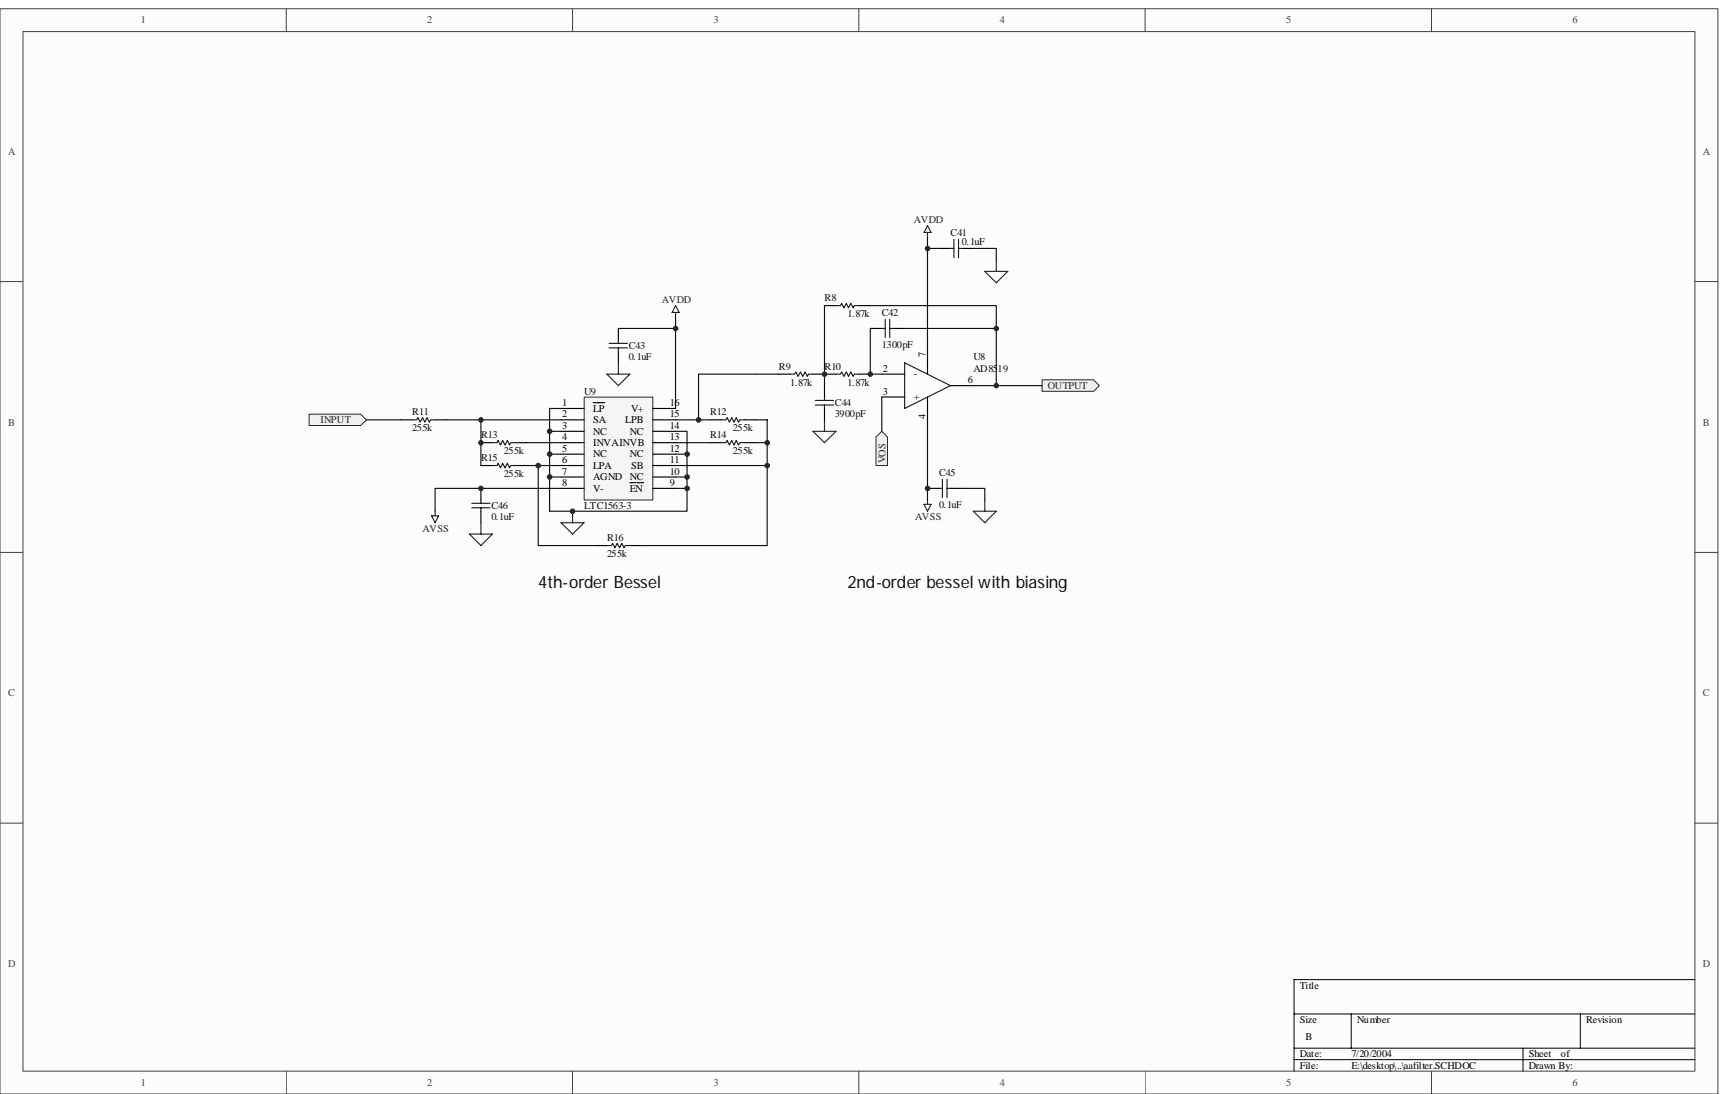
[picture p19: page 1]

Size B | Number | Revision

Date: 7/20/2004 | Sheet of
File: E:\desktop\..\aafilter.SCHDOC | Drawn By:

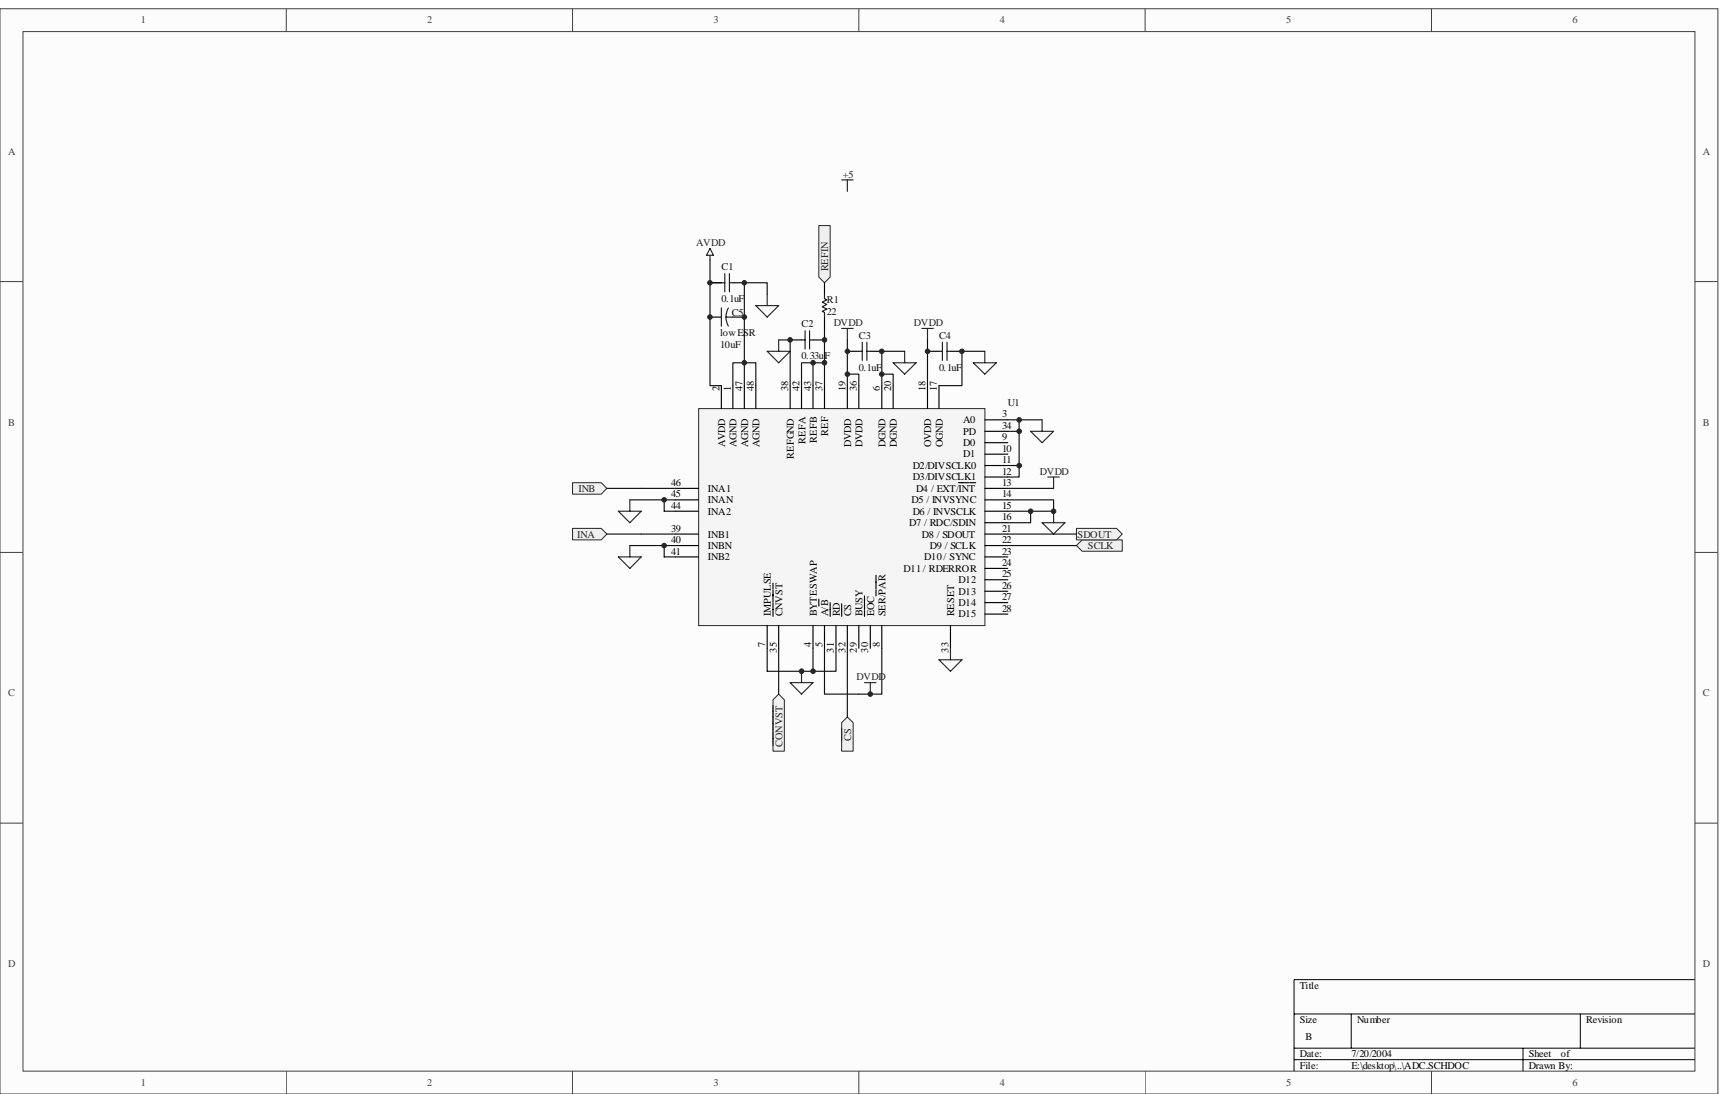
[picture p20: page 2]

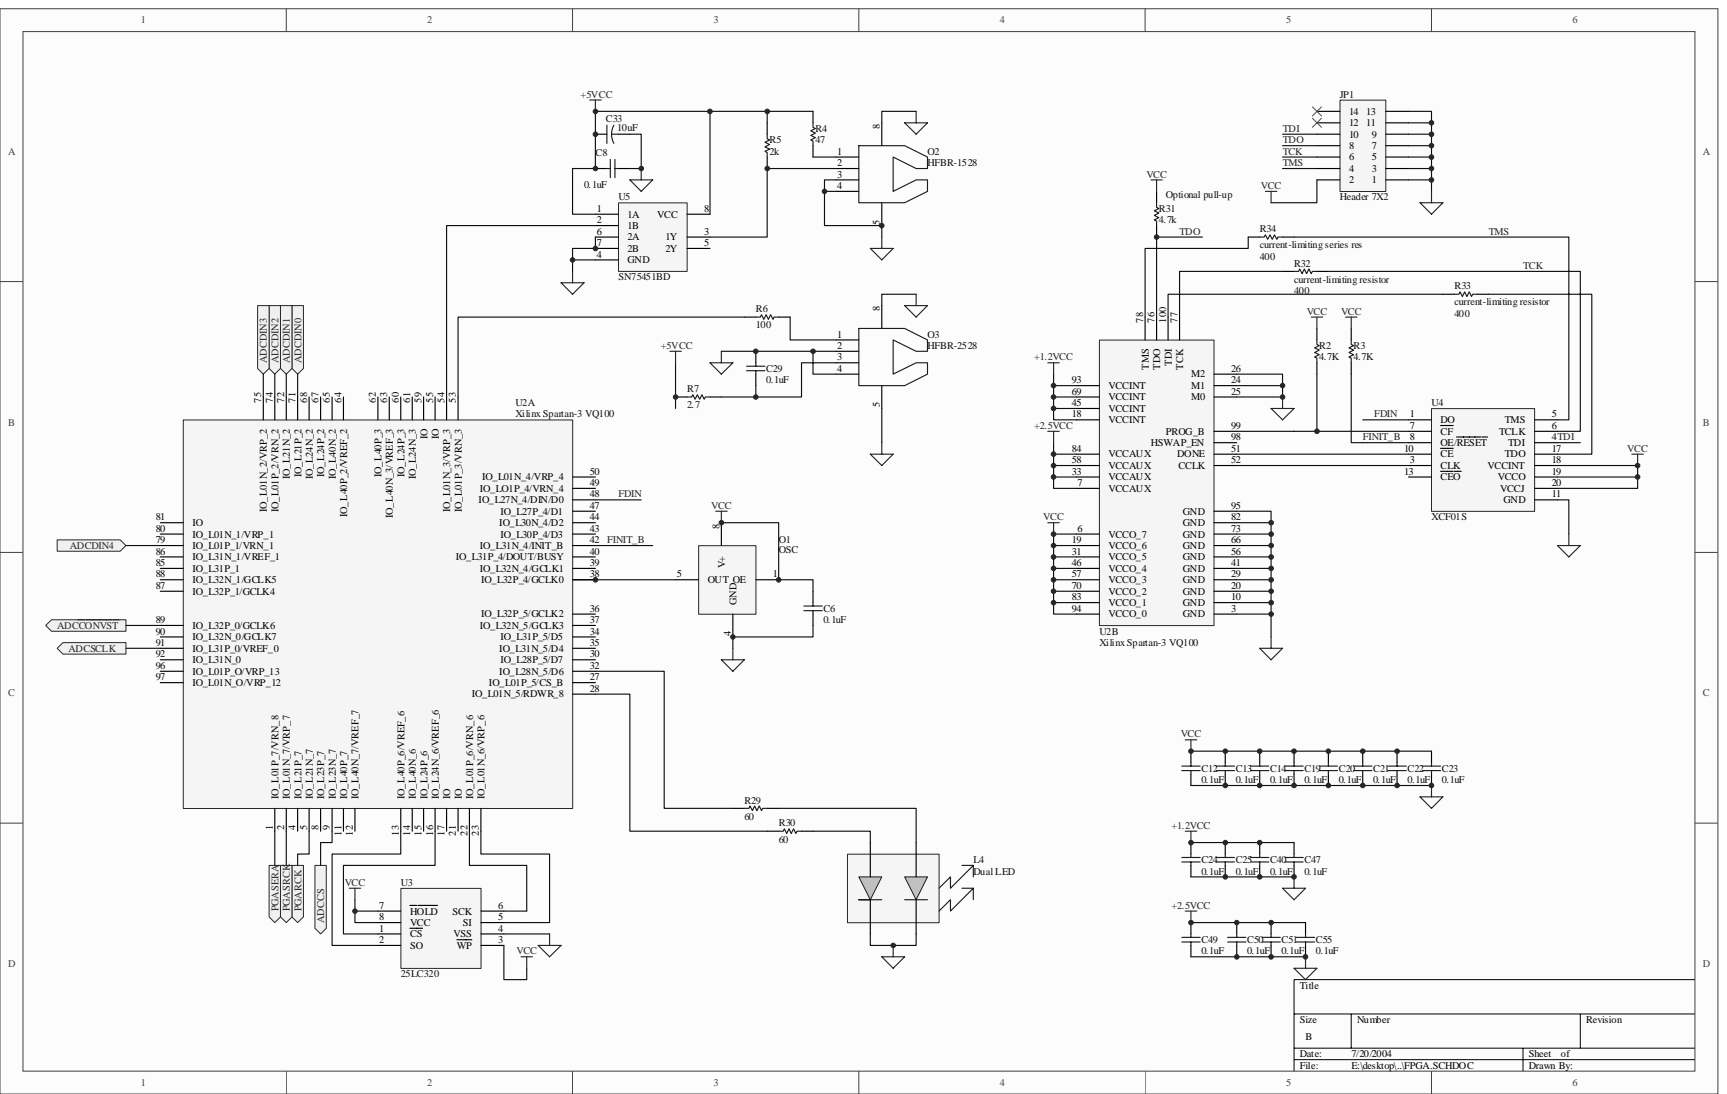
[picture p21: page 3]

TCK 77 TDI 100 TDO 76 TMS 78

+1.2VCC

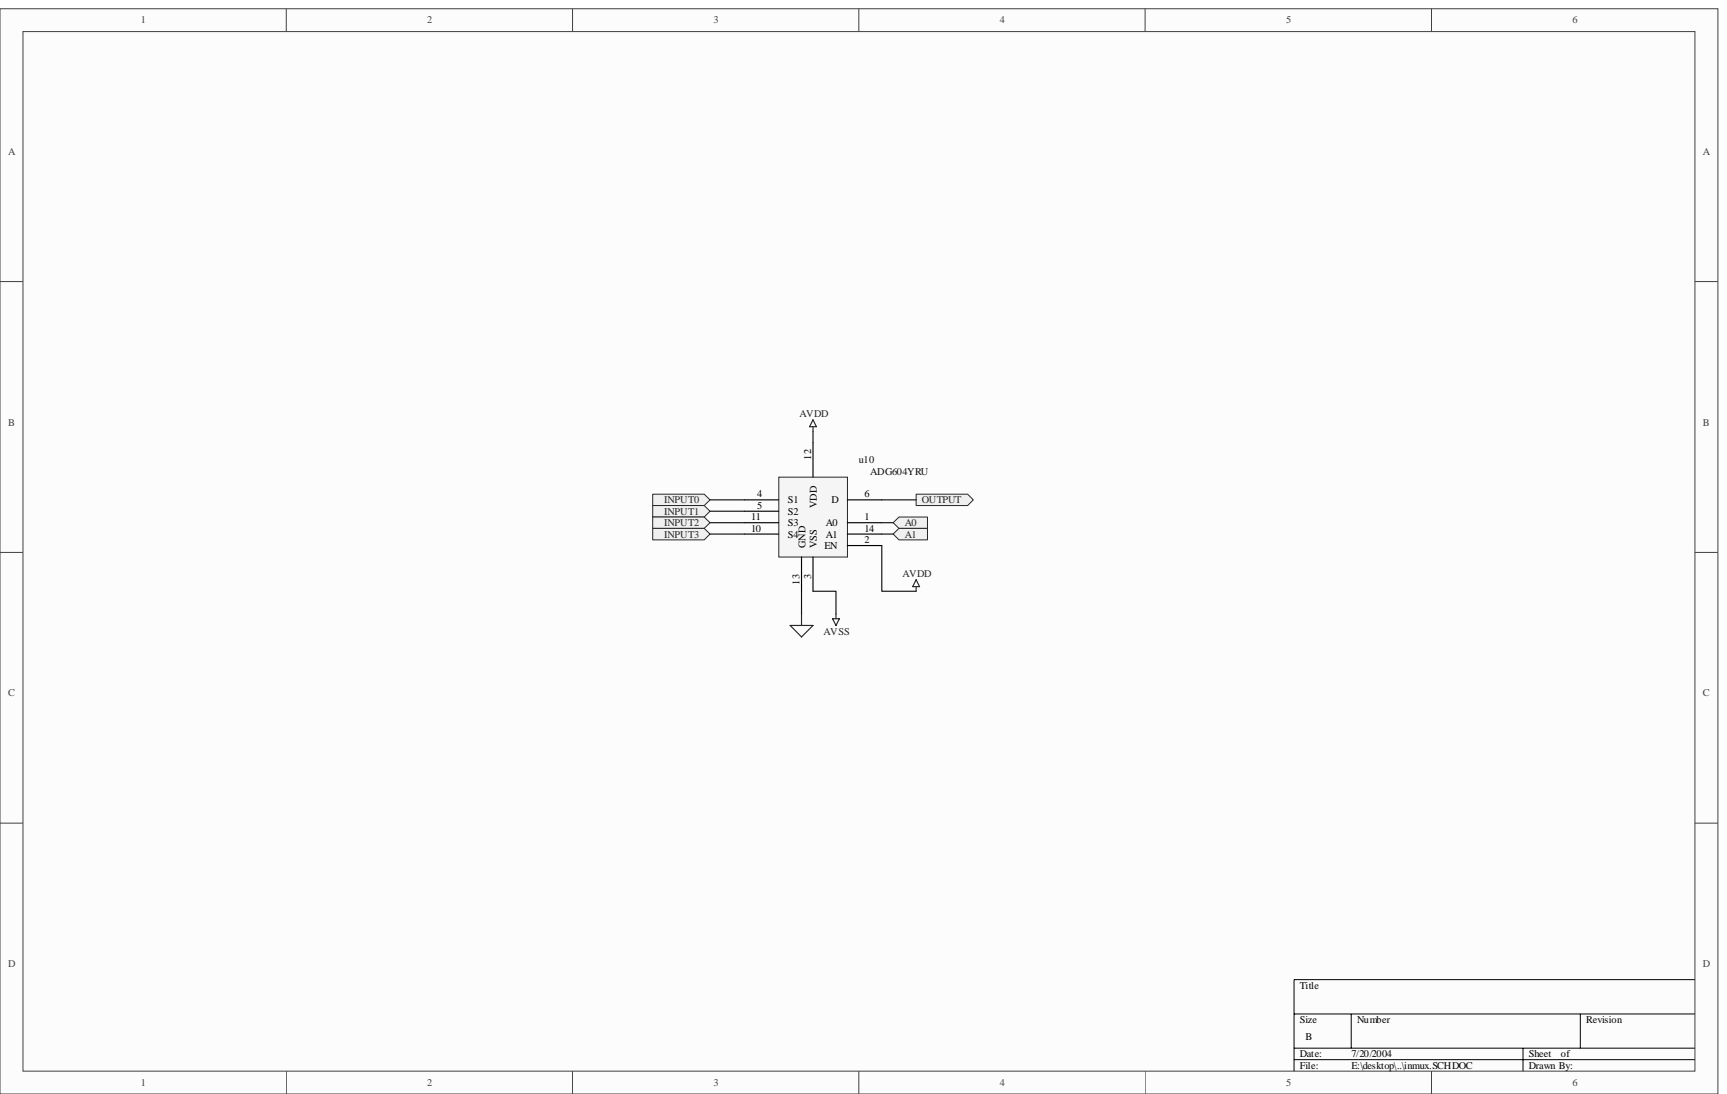
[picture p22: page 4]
File:; E:\desktop\..\inmux.SCHDOC; Drawn By:; AVDD; AVSS; INPUT0 INPUT1 INPUT2 INPUT3; OUTPUT

VDD 12 GND 13 D 6 A0 1 A1 14 EN 2 VSS 3 ADG604YRU u10

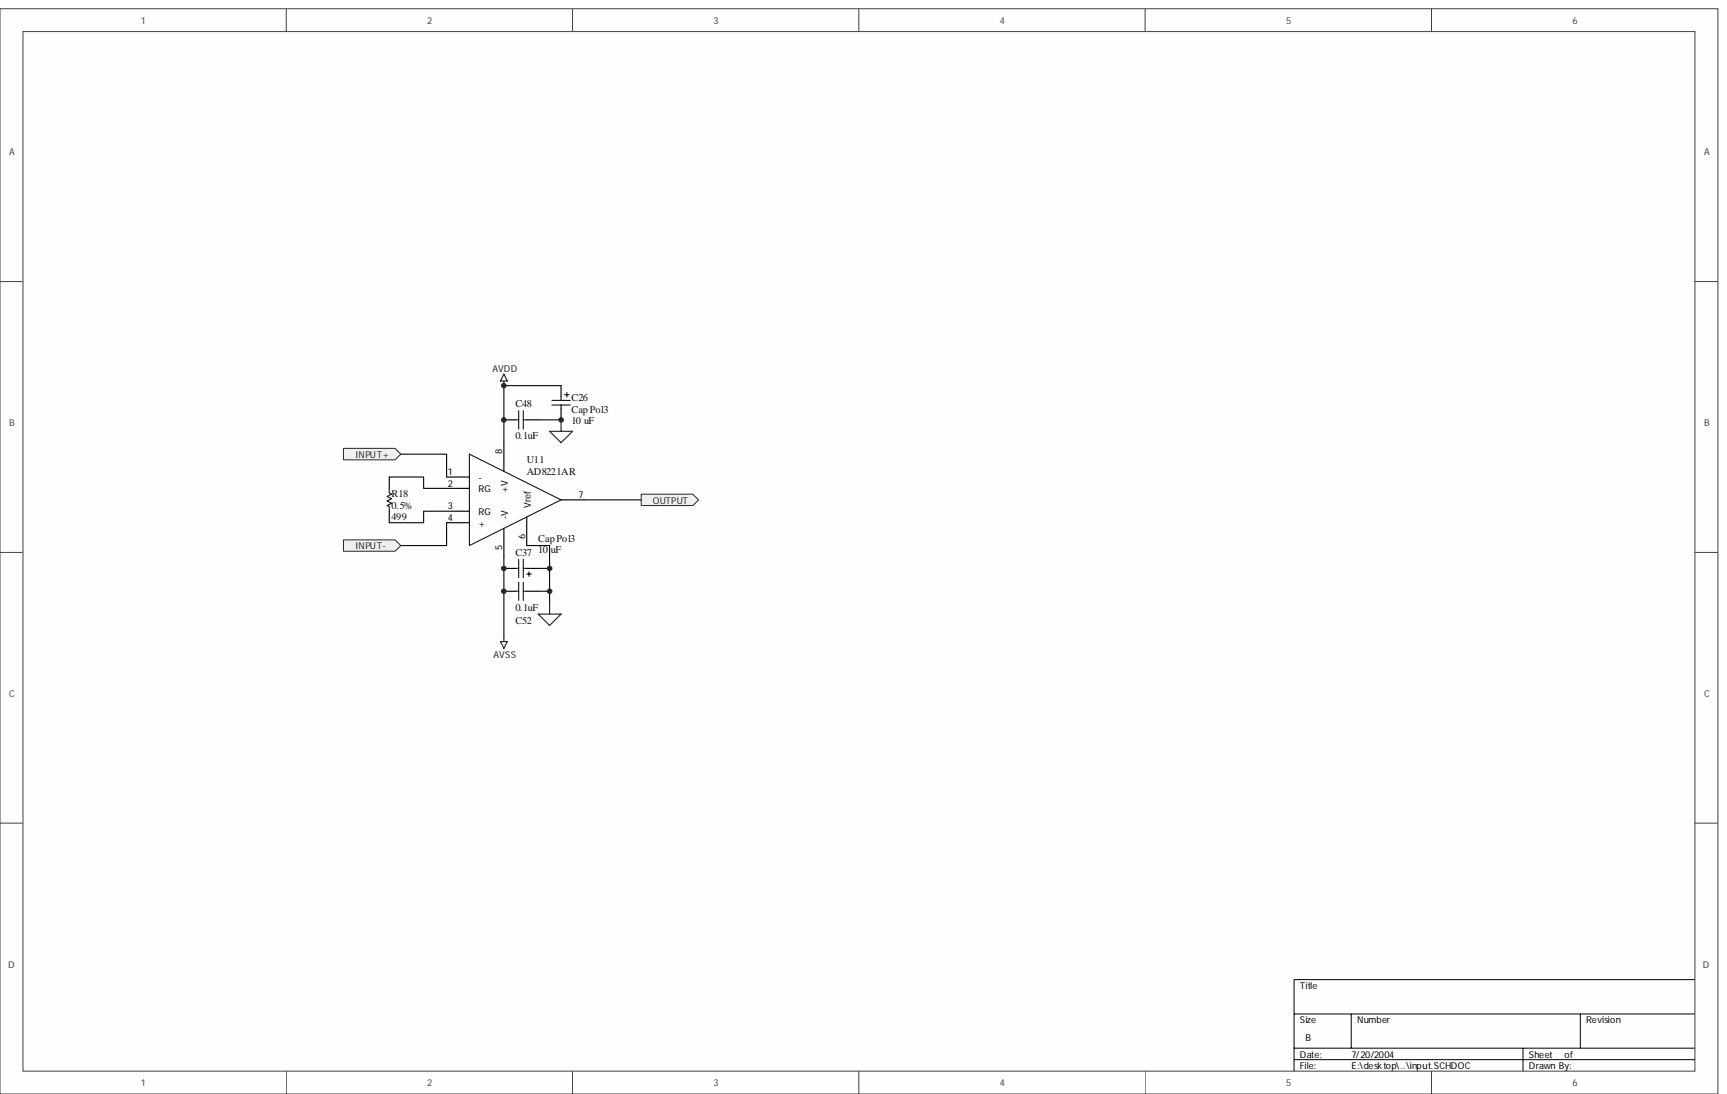
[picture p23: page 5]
File:; E:\desktop\..\input.SCHDOC; Drawn By:; Vref; INPUT+; INPUT-; AVDD; AVSS; OUTPUT; Cap Pol3

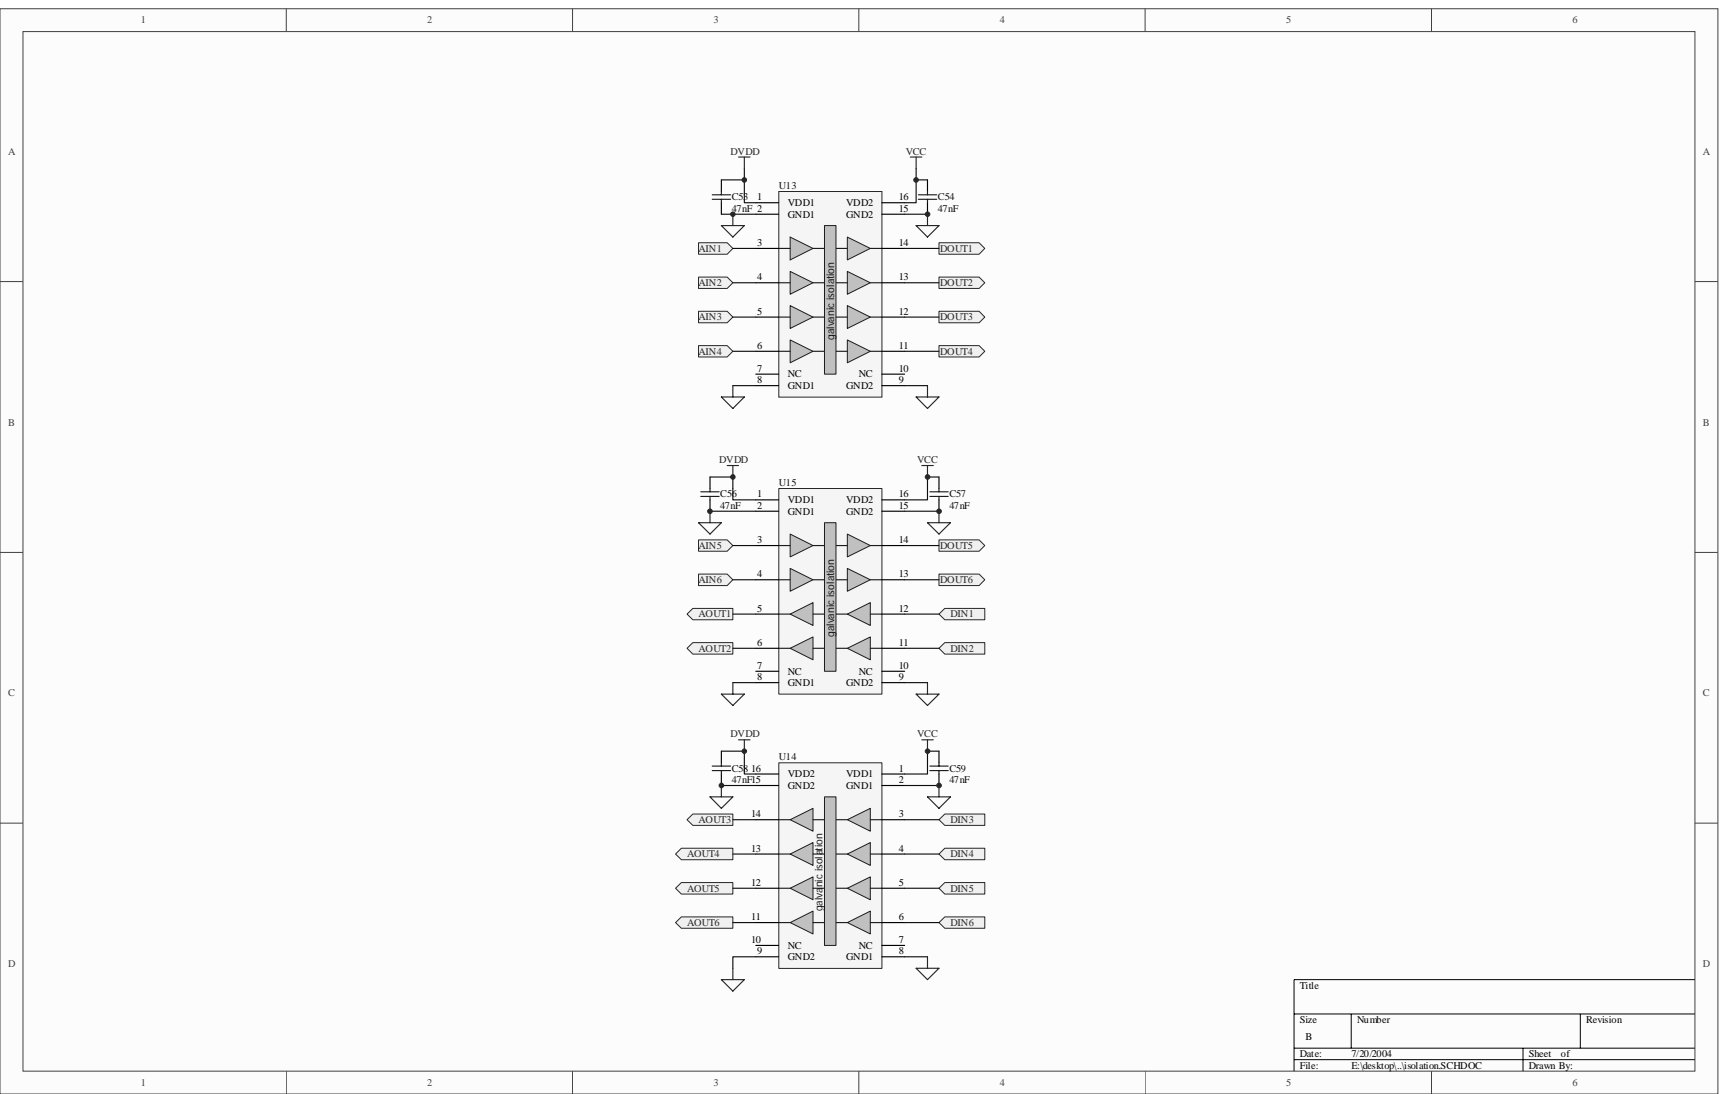
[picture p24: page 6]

File:; E:\desktop\..\main.SCHDOC; Drawn By:; REPEAT(INPUT+); REPEAT(INPUT-); REPEAT(OUTPUT); REPEAT(IN,1,8) input.schdoc; 19 20 Header 10X2H JP3; REPEAT(INPUT); VOS; repeat(AA, 1, 10) aafilter.SCHDOC; INAOUT; PGAIN; PGAIN[1..10]; INAOUT[1..8]; INAOUT1 INAOUT2 INAOUT3 INAOUT4; PGAIN1 PGAIN2 PGAIN3 PGAIN4; PGAIN7 PGAIN8 PGAIN9 PGAIN10; INAOUT5 INAOUT6 INAOUT7 INAOUT8; INPUT0 INPUT1 INPUT2; INPUT3; OUTPUT; inmux inmux.SCHDOC; PGAIN5; PGAIN6 INPUT0; INPUT1 INPUT2 INPUT3; REPEAT(SERIN); SRCLK; RCLK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


C | C31 | | AVSS | C

INMUXA INMUXB are only used by the
two PGAs closest to the input
multiplexors


Low-pass filter for digital supply on analog side

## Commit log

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2003-05-29 First attempt at using new Protel DXP. Created input, input multiplexor, PGAs and antialising filter ... still need butterworth aa filters, though, as well as consideration about compensation cap.
    [PGA.SCHDOC, aafilter.SCHDOC, acquisition board.PRJPCB, inmux.SCHDOC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]
2003-06-02 Added 8021-based two-pole butterworth with biasing to AA section. Spice simulations show that this gives correct Fc=34 kHz filtering as wel as biasing the input to 2.5V
    [PGA.SCHDOC, aafilter.SCHDOC, inmux.SCHDOC, input.SCHDOC]
2003-06-03 Added NVE isolation, power using LDO, and beagn trying to combine sheet symbols in multichannel design. I hope this works.
    [FPGA.SCHDOC, PGA.SCHDOC, aafilter.SCHDOC, acquisition board.PRJPCB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]
2003-06-07 Added voltage references with lame buffering suggested by LT, and added serial EEPROM
    [FPGA.SCHDOC, aafilter.SCHDOC, acquisition board.PRJPCB, isolation.SCHDOC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]
2003-06-12 changed value on ac-coupling HPF. Added shift registers for PGAs and inmuxes. Created DVDD power filter.
    [FPGA.SCHDOC, PGA.SCHDOC, aafilter.SCHDOC, acquisition board.PRJPCB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]
2003-06-12 Successfully placed components on acqboard without error
    [FPGA.SCHDOC, PGA.SCHDOC, acquisition board.PRJPCB, input.SCHDOC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]
2003-06-12 adding acqboard PCB
    [acqboard.PcbDoc]
2003-06-13 Almost all routed! Still need to do ADC control lines, oh, and that whole digital section too. But other than that, we're great!
    [FPGA.SCHDOC, PGA.SCHDOC, aafilter.SCHDOC, acqboard.PcbDoc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]
2003-06-15 Done with PCB layout; design passes DRC. Must now re-annotate from PCB side and then check to make sure designators don't overlap pads
    [FPGA.SCHDOC, PGA.SCHDOC, aafilter.SCHDOC, acqboard.PcbDoc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]
2003-06-15 Reannotated; correctly moved designators
    [acqboard.PcbDoc]
2003-06-15 Added nice printer settings
    [acquisition board.PRJPCB]
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2003-06-19 Added 2k resistor for I2C SDA pin
    [FPGA.SCHDOC, acqboard.PcbDoc]
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2003-06-23 Sent outputs to PCBexpress
    [acqboard.DRL, acqboard.GBL, acqboard.GBO, acqboard.GBS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]
2003-06-27 Oops, forgot to add ADC to subversion all along
    [ADC.SCHDOC]
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2003-08-04 New board design, using SPI EEPROM, HP butterworth filters. Larger 5x7 board, which has plusses and minuses. Nearly complted routnig, but for some DVDD issues.
    [ADC.SCHDOC, FPGA.SCHDOC, PGA.SCHDOC, aafilter.SCHDOC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]
2003-08-04 PCB layout done; DRC successful. Took roughly 14 hours total.
    [acqboard.PcbDoc]
2003-08-24 Wow, my committing practices are shit.
    [acqboard.PcbDoc, acquisition board.PRJPCB]
2003-10-17 Updated schematics to reflect new adc buffer OA, voltage regulators.
    [aafilter.SCHDOC, inmux.SCHDOC, power.SCHDOC]
2003-10-17 PCB AA layout updated for one channel...
    [aafilter.SCHDOC, acqboard.PcbDoc, power.SCHDOC]
2003-10-19 Okay, this has been total total hell. Protel's net renaming raelly sucks, and to make it correctly match up the ADC inputs and the AA outputs, I needed to delete a bunch of components and then recrea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
    [ADC.SCHDOC, aafilter.SCHDOC, acqboard.PcbDoc, inmux.SCHDOC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]
2003-10-19 After taking far too long, the PCB is updated with: - new op-amp for ADC buffer / level shift / 2-pole bessel - new voltage range, and new source of Vos - some nice new optional tantalums near the in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
    [FPGA.SCHDOC, acqboard.PcbDoc, input.SCHDOC, power.SCHDOC]
2003-11-13 Added status LEDs, cleaned up some PCB traces.
    [FPGA.SCHDOC, acqboard.PcbDoc]
2003-11-14 Wow, finally shipped off v 3.2. Now with status lights!
    [FPGA.SCHDOC, acqboard.DRL, acqboard.GBL, acqboard.GBS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]
2003-12-02 Wow, I haven't committed this in forever.
    I really suck. In any case, I changed the testbench behavioral entity names so that the new ISE doesn't complain too much.
    Got design to compile/synth meeting time constraints on XC2S50E.
    [acqboard.DRL, acqboard.GBL, acqboard.GBS, acqboard.GTL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]
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2004-02-23 Fixed problems with previous gerbers; enlarged pad size around some holes (LED and screws) DRC passed
    [acqboard.GBL, acqboard.GBS, acqboard.GTL, acqboard.GTO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]
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2004-03-17 component name updates
    [FPGA.SCHDOC, PGA.SCHDOC, aafilter.SCHDOC]
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2004-04-03 Changed LTC1653 to correct LTC1563.
    [aafilter.SCHDOC]
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2004-04-10 Updated some manf. numbers and part numbers on components.
    [PGA.SCHDOC, acqboard.PcbDoc, inmux.SCHDOC, input.SCHDOC]
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2004-04-17 Updated EEPROM to use correct SOIC pinout.
    [FPGA.SCHDOC, acqboard.PcbDoc]
2004-04-18 Final version of code, before we try to switch to Spartan-3
    [acqboard.PcbDoc]
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2004-04-19 Updated schematics; now we just have the PCBs to worry about.
    [FPGA.SCHDOC, power.SCHDOC]
2004-04-19 Schematics updated, PCB done, passes DRC.
    [FPGA.SCHDOC, acqboard.PcbDoc]
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2004-04-20 Set capacitor, resistor settings on HPF.
    [PGA.SCHDOC]
2004-04-20 Updated gerbers. Finally fixed "unmatched components" error.
    [acqboard.DRL, acqboard.GBL, acqboard.GBS, acqboard.GTL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]
2004-05-23 Resolved conflicts, I hope. Not sure how much I actually trust these files.
    [acqboard.DRL, acqboard.GBL, acqboard.GBS, acqboard.GTL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]
2004-05-23 Updated constraints in test setups for new FPGA. Updated FPGA to deal with updated parts lib.
    --This line, and tUpdated constraints in test setups for new FPGA.
    Updated FPGA to deal with updated parts lib.
    hose below, will be ignored--
    M acquisition board/FPGA.SCHDOC
    M acquisition board/acqboard.PcbDoc
    M tests/vhdl/constraints.ucf
    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
    [FPGA.SCHDOC, acqboard.PcbDoc]
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2004-05-25 Implemented RAW mode. Still need to debug, test. Integrated it into larger acqboard -- design still fits easily in a -50 part.
    [acqboard.GBS, acqboard.GTL, acqboard.GTO, acqboard.GTS]
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2004-05-27 Fixed a double-buffer bug in raw.vhd, added default impulse response for blockselect RAM acqcmd simulation now checks for RAW mode success
    [acqboard.PcbDoc]
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2004-06-08 Expanded power plan clearance, polygon clearance by 4 mils. Ready to reannotate
    [acqboard.PcbDoc]
2004-06-15 Umm, how unforunate that I don't commit more often.
    [FPGA.SCHDOC, acqboard.DRL, acqboard.GBL, acqboard.GBS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]
2004-06-16 Updated resistor values; changed package on jtag header so that it has correct silkscreen, hole sizes.
    [FPGA.SCHDOC, acqboard.PcbDoc, power.SCHDOC]
2004-06-21 Swapped ADC OVDD and OGND pins, made same change in parts. PCB passes DRC. About to re-annotate.
    [ADC.SCHDOC, acqboard.PcbDoc]
2004-06-21 updated gerbers
    [acqboard.DRL, acqboard.GBL, acqboard.GBS, acqboard.GTL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]
2004-06-30 Commit before transferring to new machine
    [acqboard.PcbDoc, acquisition board.PRJPCB]
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2004-11-22 New THD+N numbers on HPF design, settlingon the one compatible with the 8+2 cchannel design; redesigned schematics, switching to A paper.
    [ADC.SCHDOC, FPGA.SCHDOC, PGA.SCHDOC, aafilter.SCHDOC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]
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2004-12-02 Decided to say screw you to the OO approach, and just using a 64-bit int as a 16.48 fixed.
    [acqboard.SLDASM]
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2004-12-09 Fixed FDIN/FINIT not actually being connected to the FPGA.
    [FPGA Power.SCHDOC, FPGA.SCHDOC, acqboard.PcbDoc, main.SCHDOC]
2004-12-09 Sent a new (4.1) acquisition board to PCBpro, should get back by next wednesday. Very expensive. We:
    * added pullup resistors on serial outputs of ADCs
    * added resistors to reduce CS, SCLK, CONVST ringing
    * attempted to rectify recent problems by distributing DVDD.
    [ADC.SCHDOC, aafilter.SCHDOC, acqboard.GBL, acqboard.GBS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]
2004-12-17 Problems found on both acqboard PCB and enclosure; enclosure will necessitate redesign from home.
    [Amp 103311-5.SLDPRT, PCB.SLDPRT, acqboard.PcbDoc, acqboard.SLDASM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]
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2005-01-04 * Fixed the dreaded JTAG interface problem; just getting a new board built.
    [acqboard.GBL, acqboard.GBS, acqboard.GTL, acqboard.GTO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]
2005-01-14 * updated hole size to 140 mil; old size of 100 mil was way too small
    [acqboard.PcbDoc, power.SCHDOC]
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2005-01-21 Acqboard 4.3 works in so far as the ADC outputs real clean values; this was never a mixed signal problem at all, it's all on the FPGA side. Thank god for the logic analyzer.
    [initial.data.csv]
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2005-02-26 * updated all schematics to use the updated component library parts * Added results from jitter measurements via nice scope * added noise measurement results
    [ADC.SCHDOC, FPGA Power.SCHDOC, FPGA.SCHDOC, PGA.SCHDOC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]
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2005-09-21 * Results of past three days of board work -- great THD+N numbers up to HPF; offset issues with PGA continue to confound * Began creation of signal channel and device parameter documentation
    [ADC.SCHDOC, FPGA.SCHDOC, PGA.SCHDOC, aafilter.SCHDOC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]
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2005-12-11 * Fixed cut-out error on acqboard * updated pcb/sch component links
    [acqboard.PcbDoc, main.SCHDOC]
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2006-04-03 * Final with correct revision number, 1.1
    [acqboard.GBL, acqboard.GBP, acqboard.GBS, acqboard.GTL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]
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2006-05-20 * put fudicials on bottom side of board (Fixes #5) * Added U1 footprint to local database and fixed rotation issues (Fixes #1) * Fixed Oscillator footprint (Fixes #2)
    [ADC.SCHDOC, acqboard.PcbDoc, main.SCHDOC, parts.PCBLIB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]
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
